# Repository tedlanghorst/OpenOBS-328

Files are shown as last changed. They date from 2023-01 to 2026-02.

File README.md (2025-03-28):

# OpenOBS-328

OpenOBS-328 is the successor to the [OpenOBS](http://www.github.com/tedlanghorst/openobs) project, an opensource, field-deployable, optical backscatter sensor (OBS). OBSs are used for measuring the turbidity, or clarity, of water for environmental monitoring. Here you will the find folders for the PCB assembly files, sensor firmware, and processing scripts.

**For more information on building, deploying, and using the sensor, visit our [documentation page!](https://tedlanghorst.github.io/OpenOBS-328/)**

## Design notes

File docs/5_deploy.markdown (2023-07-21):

---
layout: page
title: Deploy
permalink: /deploy/
---

## Introduction
{:.no_toc}

This guide will take you through programming an OpenOBS-328 sensor for deployment. You will need a computer (preferably windows), a micro usb cable, an OpenOBS-328, and a AA-sized Li-ion or LiSOCL2 battery. If you have a windows computer, you can use the graphical user interface (GUI) to quickly deploy or update the firmware. Alternatively, you can compile and upload the source code directly.

**Most of this guide describes setting up your computer, which requires an internet connection for downloading files and troubleshooting issues. You will only need to do these steps once per computer.**

## Table of Contents 
{:.no_toc}
* TOC
{:toc}

## Programming
At this stage, your OpenOBS-328 should have the firmware installed, but still we need to update the current time and send over our deployment settings. The GUI is the easiest and fastest way to upload settings, or even flash pre-compiled firmware, but only works on Windows computers. On other platforms, or if you need more control over the logger firmware, you can edit the firmware, recompile, and upload using the Arduino code editor.

---
### GUI
#### Setup
1. All of the latest OpenOBS GUI files and documentation are available in a seperate [github repo](https://github.com/tedlanghorst/OpenOBS-GUI). Download the github repository and then navigate to *OpenOBS-GUI/bin/* and try to run the *OpenOBS_328_GUI.exe* application. The program will only run on a Windows computer with the .NET 5 Desktop Runtime. If you don’t have the correct runtime, an error will pop up and direct you to the download page.

1. Connect an OpenOBS-328 sensor to your computer with a micro USB cable to test your setup.

1. Click the dropdown menu at the top of the deploy GUI and select the COM port that corresponds to the OpenOBS. You can identify the right port by trial and error (press the connect button and wait a few seconds), or by noting the available COM ports, disconnecting the OpenOBS, opening the dropdown again to refresh the list, and checking which COM port has disappeared. 
    * If you can not find the OpenOBS COM port, you likely need to download and install the [CH340 USB-Serial driver](https://learn.sparkfun.com/tutorials/how-to-install-ch340-drivers/all#drivers-if-you-need-them) on your computer.
    * If you still can not find the COM port, you may need to reflash the firmware on the sensor. Try following the steps in the next [next section.](#arduino-code)
1. After connecting to an OpenOBS, the sensor will go through a startup and self checkout before letting you program it. Any errors will be displayed on the right side of the GUI along with possible solutions. If there are no errors, the “Send Settings” button will be enabled and turn green while the sensor waits for you to choose the deployment settings:

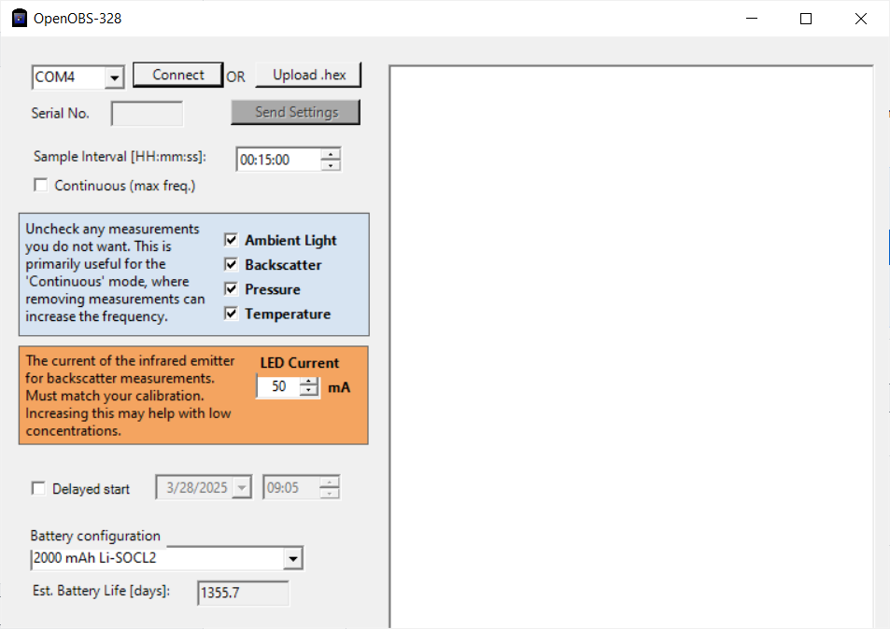
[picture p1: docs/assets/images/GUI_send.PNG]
Connected GUI
    

1. At this point you have successfully set up the deployment GUI. Good job! If you use the same USB port in the future, the COM port should be the same every time you connect an OpenOBS.

#### Deploying
1. Open the OpenOBS and slide the circuit board out of the PVC housing. Install a 3.6V Li-SOCl2 or 3.7V Li-ion AA-size battery. 
    >:warning: A regular 1.5V AA battery (even the lithium types) will not work. The USB connection provides power while plugged in, so you will not have any indication that the battery is working while programming the sensor. 
1. Connect the OpenOBS Arduino and the computer with a micro USB cable.
1. Open the deployment GUI program.
1. Select the correct COM port and click “Connect”.
1. If there are no errors on startup, the “Send Settings” button will be enabled and turn green while the sensor waits for you to choose the deployment settings.
1. Enter your sampling interval. Select delayed start if you want the logger to sleep until the set time. In addition to setting the measurement interval, sending the settings to the OpenOBS synchronizes the clock with your computer. Make sure your computer time is accurate and set to your time zone of choice, as there are no time zones recorded on the OpenOBS.
1. Selecting the battery from the dropdown will give you an estimate of the battery life. Be conservative with these numbers, they are extrapolations of short term measurements and not fully tested. Our best estimates (and tests) of battery life are here:

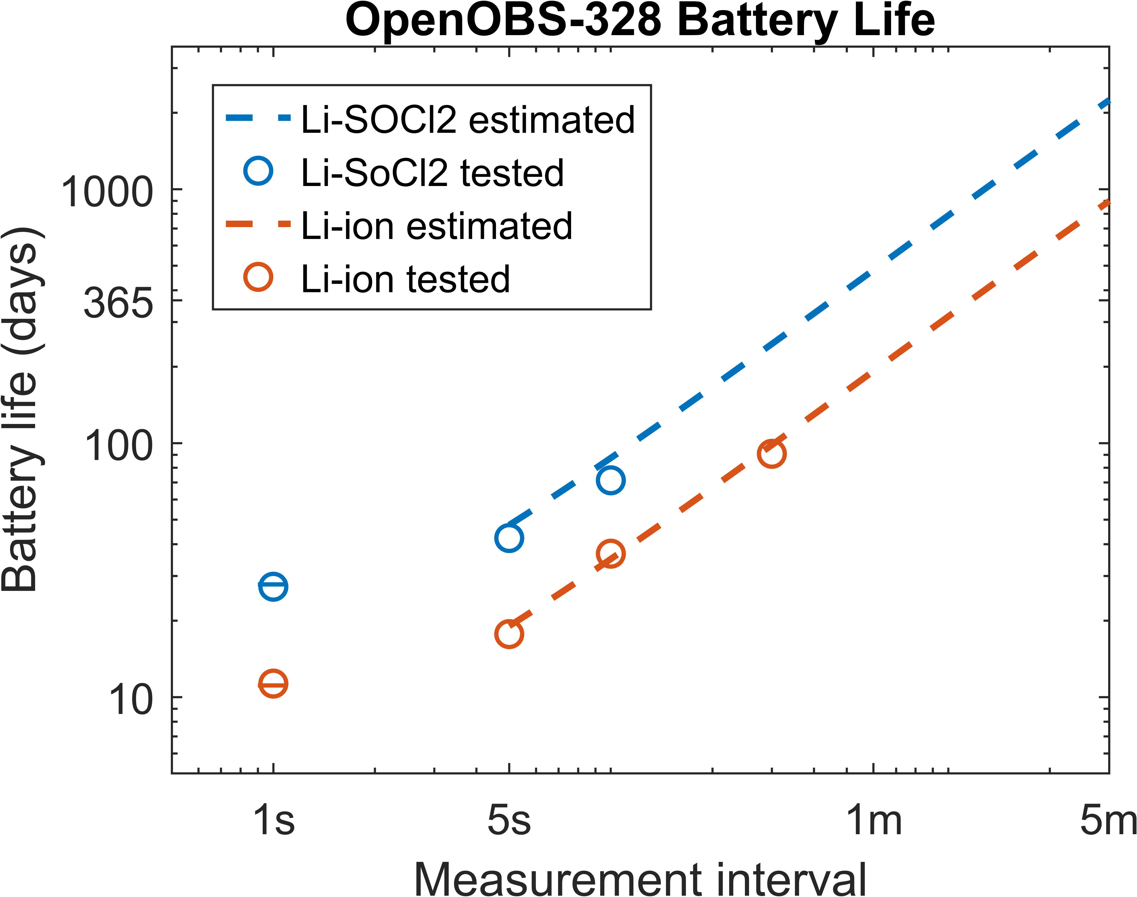
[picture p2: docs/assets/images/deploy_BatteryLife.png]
battery life
    

1. Click “Send Settings”. The OpenOBS will print out raw data when it logs while connected, refer to the [data page](./5_data.markdown) to interpret it. 

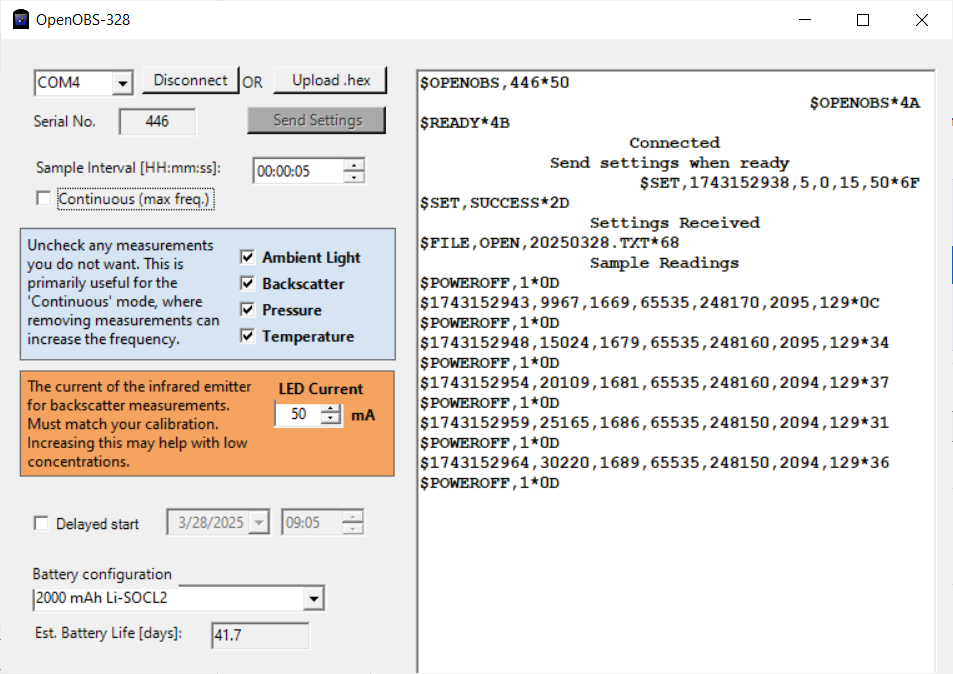
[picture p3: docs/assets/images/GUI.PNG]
programmed sensor
    

### Arduino Code
1. This option is nearly identical to the steps required to set up a newly-constructed sensor. Follow the programming directions on the [build page](./2_build.markdown#programming).
1. Change the variable *sleepDuration_seconds* to set the measurement interval. 
1. Change *delayedStart_seconds* if desired.
1. When you upload the code, the compiler will take the time from your computer, so make sure it is accurate and in the right time zone you want to record in the data.

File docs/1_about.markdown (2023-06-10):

---
layout: page
title: About
permalink: /about/
---

OpenOBS is an academic research project to develop an open source, affordable, and accurate turbidity and water level sensor using common electronics components. Turbidity (which can be calibrated to the concentration of suspended particulate matter) and water level (which can be calibrated to river discharge) are key components of monitoring a river system. Increased flow in the river raises the water level, and at the same time, washes sediment and other matter downstream. OpenOBS-328 allows us to cheaply and effectively monitor both of these effects. While comparable commercial sensors cost upwards of $2000, OpenOBS can be built for about $50 and a couple hours of work. 

&nbsp;

# History 
The project began at the University of North Carolina at Chapel Hill (UNC) under the direction of Dr. Evan Goldstein and Dr. Emily Eidam in 2019. After a long period of design and testing, we started producing dozens of sensors and published [the first OpenOBS manuscript](https://aslopubs.onlinelibrary.wiley.com/doi/abs/10.1002/lom3.10469) in Limnology and Oceanography Methods. By 2022, we had built almost 90 sensors and deployed them many times in North Carolina and Alaska, USA. Constructing each sensor was labor intensive and often required troubleshooting problems after assembly. Further, readings were highly sensitive to ambient light and affected by changes in temperature. 

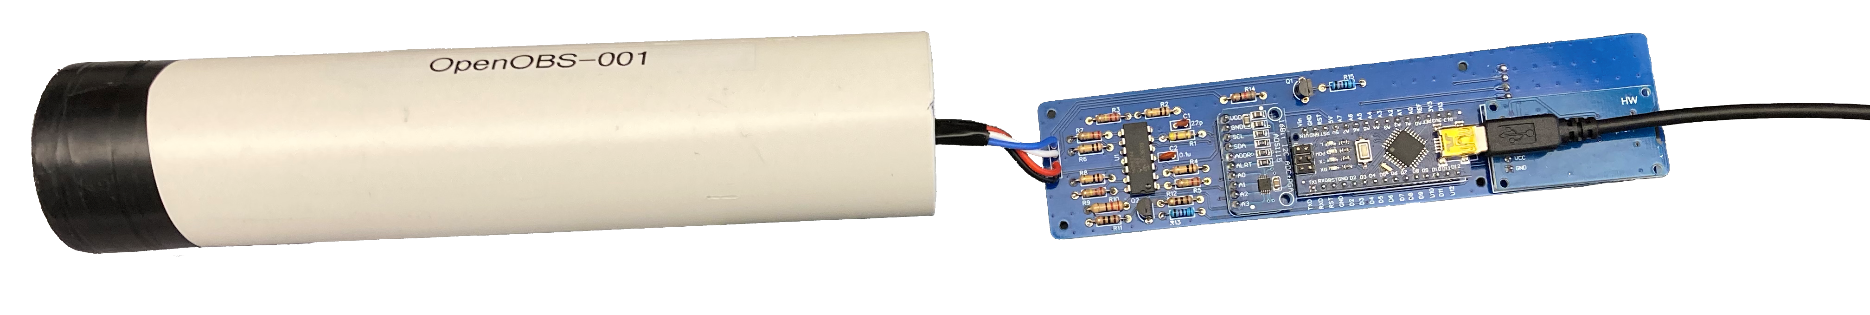
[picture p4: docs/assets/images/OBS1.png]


*The Original OpenOBS sensor ([GitHub repo](https://github.com/tedlanghorst/OpenOBS)).*

&nbsp;

Development of the OpenOBS-328 began in Fall 2022 when Dr. Emily Eidam was awarded an NSF grant which provided funding to continue developement of the OpenOBS sensor. This included the addition of the pressure sensor and a variant that transmits data in real time. At this point, we decided to move on from many of the old design decisions and approach the problem again with our new knowledge. We changed from a discrete implementation of a photodiode and signal amplifier to an integrated solution (the VCNL4010), which uses the same measurement principles and handles all the analog sensing. We also transitioned from hand-soldering modules on a printed circuit board (PCB) to an entirely assembled PCB that integrated the same functions in a smaller package.

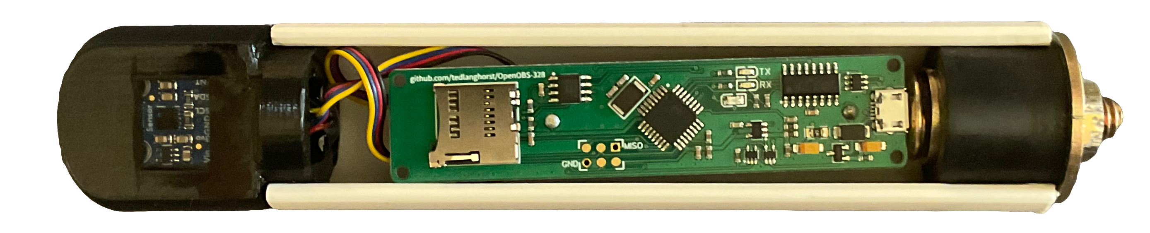
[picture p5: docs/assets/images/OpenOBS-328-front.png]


*The new OpenOBS-328 sensor.*

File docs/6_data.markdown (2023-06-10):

---
layout: page
title: Data
permalink: /data/
---

## Data format
Data is saved on the micro SD card as a .TXT file. A new file is created every day at midnight with the format YYYYMMDD. The data files should look something like this: 
~~~
If found, please contact XXXXX
Firmware updated: 2023/02/27
OpenOBS SN:000

time,ambient_light,backscatter,pressure,water_temp,battery
1677518326,1307,11354,9823,2145,649
1677518327,1300,11360,9826,2145,641
1677518328,2402,11296,9824,2145,639
1677518329,3068,11273,9824,2145,639
1677518330,2218,11287,9823,2146,639
~~~

After the data header, we have columns of data that represent
* time (Posix/Unix time. seconds since Jan 1, 1970)
* ambient light (light from 400-700 nm. Appx. equal to 1-2 Lux per unit)
* backscatter (uncalibrated backscatter intensity. Linear w.r.t. turbidity)
* pressure (bar * 10<sup>-5</sup>)
* water temperature (C * 10<sup>-1</sup>)
* battery level (multiply by 3.3*2<sup>-9</sup> to get Volts)

*There is an intermittent bug in the firmware that occasionally omits the header. If this happens, don't worry. The data rows are unaffected and you can copy a header over from another day (make sure you keep the serial number the same).*

## Iridium logger data
The Iridium data logger uses the same sensor head as the 328 version, but with an additional air pressure and temperature sensor for water level correction. As such, the data files on the micro-SD card look very similar to the 328 data. 
The data transmitted from the Iridium loggers is the same as stored on the micro-SD card, but has to be unpacked after transmitting. Rockblock charges about $0.12 per 50 bytes of data transmitted, so we use bit field structures to pack the data down to the smallest possible size without losing information. Each data record is packed into 16 bytes as follows: 

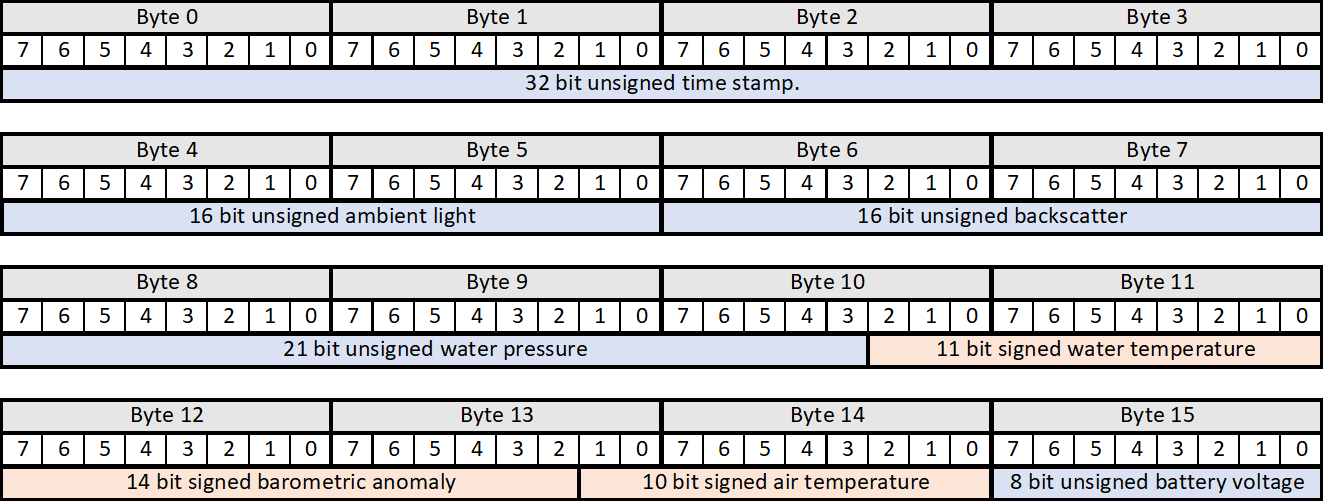
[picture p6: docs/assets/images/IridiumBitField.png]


The Iridium loggers batch these data and transmits 3 sets of 16 bytes (48 bytes) at once, to fit nicely in the 50 byte Iridium package. When you receive the data, it will have some header info and then a string of characters representing the bytes in hexadecimal. You will need to process the data according to the image above before using it.

Below is an example script in python that parses the data using the ctypes package and carefully recreating our data structure and union with a byte array. This mimicks what happens when we package the data before transmitting, except instead of putting measurements into the records in our transmission packet, we put the data string into the packet. Then, we can access the measurements records through the packet union object.

~~~python

import ctypes as ct

#example data
dataString = "320254641900E72A8884811B2FFF36883E0254641900F52A8784811B36FF3685480254641A00F82A8A84811B34BF3685"
dataBytes = bytes.fromhex(dataString)
nBytes = len(dataBytes)

#recreate the data structure from the Arduino data logger
class single_record(ct.LittleEndianStructure):
    _fields_ = [("logtime", ct.c_uint32, 32),
                ("tuBackground", ct.c_uint32, 16),
                ("tuBackscatter", ct.c_uint32, 16),
                ("waterPressure", ct.c_uint32, 21),
                ("waterTemp",ct.c_int32, 11),
                ("baroAnomaly",ct.c_int32,14),
                ("airTemp",ct.c_int32,10),
                ("batteryVoltage",ct.c_uint32,8)]  
    
class transmission_packet(ct.Union):
    _fields_ = [("record", single_record*(nBytes//ct.sizeof(single_record))),
                ("data", ct.c_ubyte*nBytes)]

#Create a packet object and put our data in as a byte array.
packet = transmission_packet()
packet.data = (ct.c_ubyte * nBytes)(*dataBytes)

#example data access
print(packet.record[0].logtime)

#show all the data
for r in packet.record:
    for f in r._fields_:
        print('{:<20s}{:d}'.format(f[0], getattr(r, f[0])))

~~~

## Processing scripts
Some basic processing scripts for Matlab and Python are found [here](https://github.com/tedlanghorst/OpenOBS-328/tree/main/scripts). I try to keep these updated but variations in sensor versions and development can make it messy. Check over the data headers and conversions if you use them.

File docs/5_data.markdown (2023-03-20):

---
layout: page
title: Data
permalink: /data/
---

## Data format
Data is saved on the micro SD card as a .TXT file. A new file is created every day at midnight with the format YYYYMMDD. The data files should look something like this: 
~~~
If found, please contact tlang@live.unc.edu
Firmware updated: 2023/02/27
OpenOBS SN:000

time,ambient_light,backscatter,pressure,water_temp,battery
1677518326,1307,11354,9823,2145,649
1677518327,1300,11360,9826,2145,641
1677518328,2402,11296,9824,2145,639
1677518329,3068,11273,9824,2145,639
1677518330,2218,11287,9823,2146,639
~~~

After the data header, we have columns of data that represent
* time (Posix/Unix time. seconds since Jan 1, 1970)
* ambient light (light from 400-700 nm. Appx. equal to 1-2 Lux per unit)
* backscatter (uncalibrated backscatter intensity. Linear w.r.t. turbidity)
* pressure (bar * $10^{-5}$)
* battery (multiply by $\frac{3.3}{2^{9}}$ to get Volts)

*There is an intermittent bug in the firmware that occasionally omits the header. If this happens, don't worry. The data rows are unaffected and you can copy a header over from another day (make sure you keep the serial number the same).*

## Processing scripts
Some basic processing scripts for Matlab and Python are found [here](http://www.github.com). I try to keep these updated but variations in sensor versions and development can make it messy. Check over the data headers and conversions if you use them.

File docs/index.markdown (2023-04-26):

---
# Feel free to add content and custom Front Matter to this file.
# To modify the layout, see https://jekyllrb.com/docs/themes/#overriding-theme-defaults

layout: home
permalink: 
---

Welcome to the OpenOBS documentation site! Browse the pages linked in the header for information about the project, how to build your own OpenOBS, and how to use the sensors. 

If you find an error or have a problem with any part of the project, please let us know by [**opening a new issue**](https://github.com/tedlanghorst/OpenOBS-328/issues/new). This leaves a public record of outstanding issues and solutions that can help others. 



---
&nbsp; 

OpenOBS is published under the [GNU GPL v3 license](https://www.gnu.org/licenses/gpl-3.0.en.html). In short, this license ensures the freedom of use and distribution of this project forever. You can copy this work exactly or modify it (maybe replace the image of my dog with yours), give it away or sell it; what you cannot do is redistribute the OpenOBS, or a derivative of it, without these same freedoms.

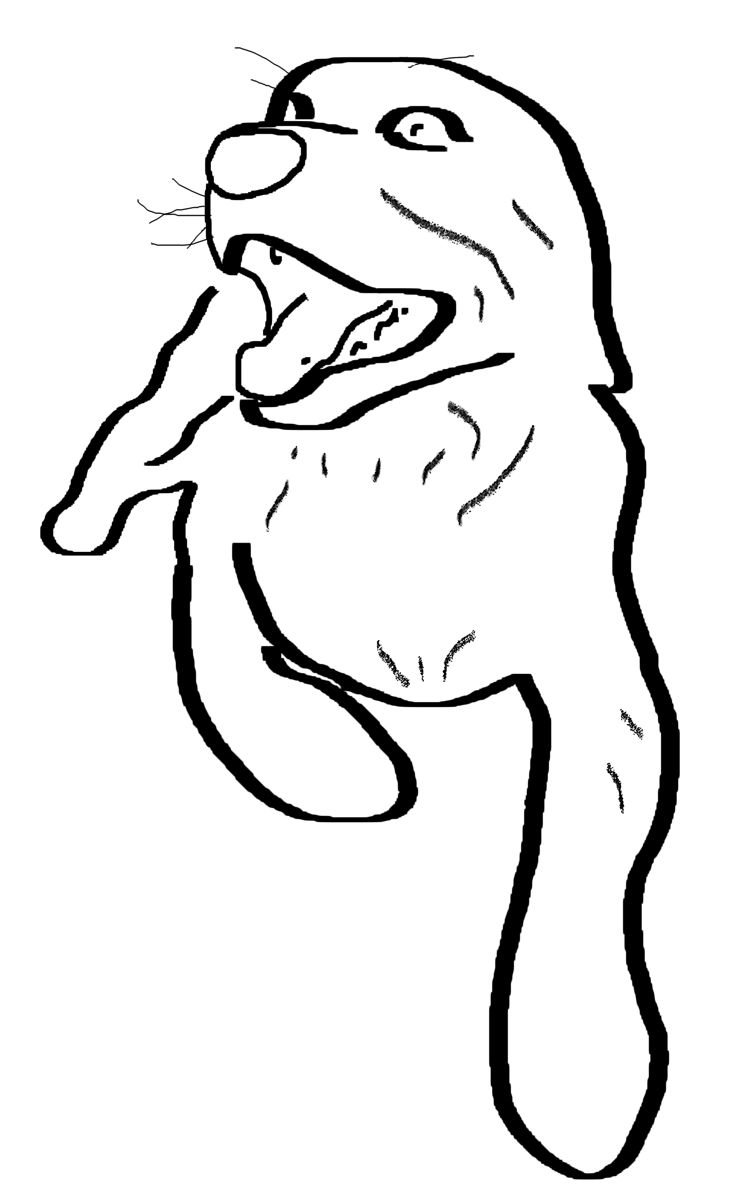
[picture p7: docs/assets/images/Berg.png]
BERG!
<p style="text-align:center;"> BERG! </p>

<!--https://docs.github.com/en/pages/setting-up-a-github-pages-site-with-jekyll/testing-your-github-pages-site-locally-with-jekyll-->

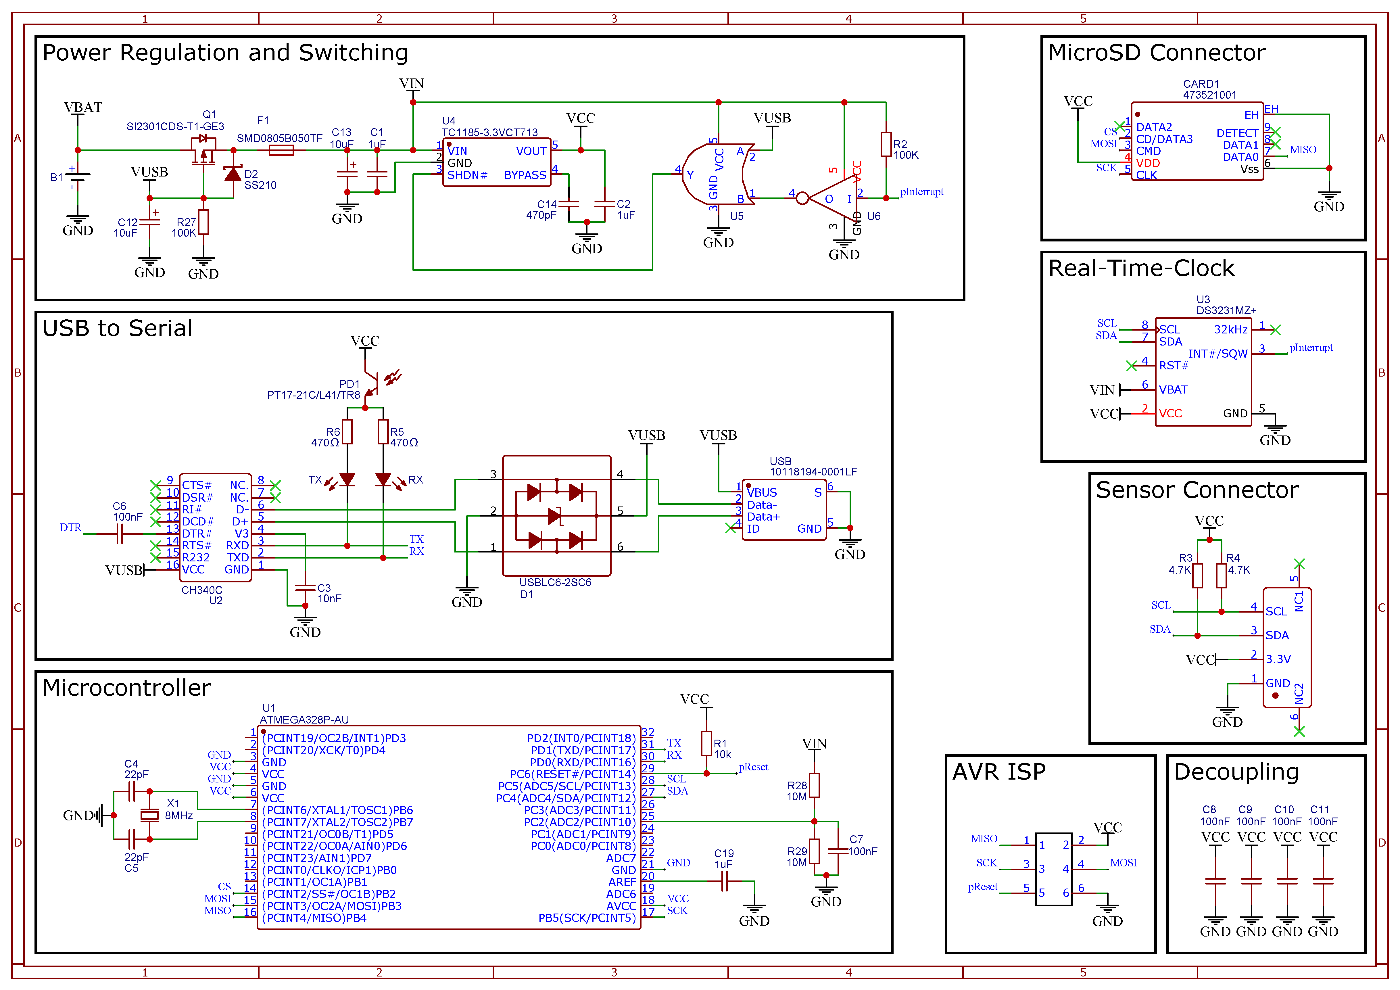
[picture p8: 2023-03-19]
docs/assets/images/Schematic_OpenOBS_328p_Tanana_2023-02-04.png

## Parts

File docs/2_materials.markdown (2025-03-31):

---
layout: page
title: Materials
permalink: /materials/
---
## Introduction
{:.no_toc}
The parts cost of an OpenOBS-328 is approximately $50 USD. This can be slightly reduced in larger quantities ($40 at 50 qty). You will also need tools and equipment to build your sensors, which we have tried to reduce to the essentials here. These costs are substantial, especially if you are trying to build just a few sensors. If you don't have a lot of this equipment and aren't looking to invest in these tools, look into community resources. For example, the Univeristy of North Caorlina at Chapel Hill has a 'makerspace' with most of these tool available. Similar spaces and tool sharing communities exist outside of univiersities. 

## Table of Contents 
{:.no_toc}
* TOC
{:toc}

## Tools & Materials
* Soldering iron
* Solder
* Hot air gun/station for electronics. (sometimes called rework station)
* No clean solder paste
* Vacuum pump
* Vacuum chamber
* disposable pipettes (3 mL size works well)
* Hot glue gun
* 3D printer
* PVC pipe cutter (can use a saw)
* PVC cement/solvent
* Electronics tweezers
* Fine flush cutters
* Wire strippers (22-30 AWG)
* Electrical tape
* micro USB cable
* Arduino Nano (or clone; [for ISP programmer](./3_build.markdown#isp-programmer))
* Pogo pins (6 individual or 2x3 grid)

## Parts

<style type="text/css">
.tg  {border-collapse:collapse;border-spacing:0;}
.tg td{border-color:black;border-style:solid;border-width:1px;font-family:Arial, sans-serif;font-size:14px;
  overflow:hidden;padding:10px 5px;word-break:normal;}
.tg th{border-color:black;border-style:solid;border-width:1px;font-family:Arial, sans-serif;font-size:14px;
  font-weight:normal;overflow:hidden;padding:10px 5px;word-break:normal;}
.tg .tg-wp8o{border-color:#000000; text-align:center;vertical-align:top}
.tg .tg-73oq{border-color:#000000;text-align:left;vertical-align:top}
.tg .tg-jdb5{border-color:#000000;font-weight:bold;text-align:center;vertical-align:bottom; border-width: 0px 0px 5px 0px}
.tg .tg-1tol{border-color:#000000;font-weight:bold;text-align:left;vertical-align:middle}
.tg .tg-4e6d{border-color:#000000;color:#00E;text-align:left;text-decoration:underline;vertical-align:top}
.tg .tg-noSides{border-left:0px; border-right:0px}
</style>
<table class="tg">
<colgroup>
<col style="width: 15%">
<col style="width: 20%">
<col style="width: 10%">
<col style="width: 10%">
<col style="width: 20%">
</colgroup>
<thead>
  <tr>
    <th class="tg-jdb5"></th>
    <th class="tg-jdb5">Item</th>
    <th class="tg-jdb5">Appx. Cost</th>
    <th class="tg-jdb5">Links</th>
    <th class="tg-jdb5">Notes</th>
  </tr>
</thead>
<tbody>
  <tr>
    <td class="tg-1tol" rowspan="10">Sensor head</td>
    <td class="tg-73oq">3D printed head</td>
    <td class="tg-wp8o">0.50</td>
    <td class="tg-73oq"><a href="https://github.com/tedlanghorst/OpenOBS-328/tree/main/sensor/hardware/3D_print/custom_pcbs" target="_blank" rel="noopener noreferrer">files</a></td>
    <td class="tg-73oq"></td>
  </tr>
  
  <tr>
    <td class="tg-73oq">m3x6 bolt</td>
    <td class="tg-wp8o">0.10</td>
    <td class="tg-73oq"><a href="https://www.amazon.com/Socket-Screws-Bolts-Thread-100pcs/dp/B07CMRQ3TB?crid=85QEXH6R1XAD&th=1" target="_blank" rel="noopener noreferrer">Gerber files</a></td>
    <td class="tg-73oq">ordering instructions below</td>
  </tr>
  <tr>
    <td class="tg-73oq">Light sensor</td>
    <td class="tg-wp8o">2.50</td>
    <td class="tg-73oq"><a href="https://github.com/tedlanghorst/OpenOBS-328/tree/main/sensor/hardware/PCBA/turbidity" target="_blank" rel="noopener noreferrer">Gerber files</a></td>
    <td class="tg-73oq">ordering instructions below</td>
  </tr>
  <tr>
    <td class="tg-73oq">pressure PCB</td>
    <td class="tg-wp8o">0.40</td>
    <td class="tg-73oq"><a href="https://github.com/tedlanghorst/OpenOBS-328/tree/main/sensor/hardware/PCBA/pressure" target="_blank" rel="noopener noreferrer">Gerber files</a></td>
    <td class="tg-73oq">ordering instructions below</td>
  </tr>
  <tr>
    <td class="tg-73oq">pressure sensor</td>
    <td class="tg-wp8o">21</td>
    <td class="tg-73oq"><a href="https://octopart.com/ms580314ba01-00-te+connectivity-59208930?r=sp" target="_blank" rel="noopener noreferrer">14 bar</a><br><a href="https://octopart.com/ms580305ba01-00-te+connectivity-59208929?r=sp" target="_blank" rel="noopener noreferrer">5 bar</a></td>
    <td class="tg-73oq">5 bar max sensor has better resolution</td>
  </tr>
  <tr>
    <td class="tg-73oq">flat flex cable</td>
    <td class="tg-wp8o">0.61</td>
    <td class="tg-73oq"><a href="https://octopart.com/search?q=5-1474644-0&currency=USD&specs=0" target="_blank" rel="noopener noreferrer">octopart</a></td>
    <td class="tg-73oq"></td>
  </tr>
  <tr>
    <td class="tg-73oq">0603 0.1uF</td>
    <td class="tg-wp8o">0.01</td>
    <td class="tg-73oq"><a href="https://octopart.com/cl10b104kb8nnwc-samsung-23795471?r=sp" target="_blank" rel="noopener noreferrer">octopart</a></td>
    <td class="tg-73oq">Very generic part. Any 0603 0.1uF will do.</td>
  </tr>
  <tr>
    <td class="tg-73oq">epoxy</td>
    <td class="tg-wp8o">0.50</td>
    <td class="tg-73oq"><a href="https://www.amazon.com/dp/B07RM5Z991" target="_blank" rel="noopener noreferrer">750g</a><br><a href="https://www.amazon.com/dp/B079Y9QFQS/" target="_blank" rel="noopener noreferrer">1500g</a></td>
    <td class="tg-73oq">~20g per sensor</td>
  </tr>
  <tr>
    <td class="tg-73oq">1" PVC</td>
    <td class="tg-wp8o">0.40</td>
    <td class="tg-73oq"><a href="https://www.lowes.com/pd/1-in-dia-x-10-ft-L-450-PSI-PVC-Pipe/3133091" target="_blank" rel="noopener noreferrer">Lowe's</a></td>
    <td class="tg-73oq">6" per sensor</td>
  </tr>
  <tr>
    <td class="tg-73oq">pvc cement</td>
    <td class="tg-wp8o">0.20</td>
    <td class="tg-73oq"><a href="https://www.lowes.com/pd/Oatey-8-fl-oz-PVC-Cement/4750803" target="_blank" rel="noopener noreferrer">Lowe's</a></td>
    <td class="tg-73oq">cost based on 50 sensors</td>
  </tr>
  <tr>
    <td class="tg-noSides"></td>
    <td class="tg-noSides"></td>
    <td class="tg-noSides"></td>
    <td class="tg-noSides"></td>
    <td class="tg-noSides"></td>
  </tr>
  <tr>
    <td class="tg-1tol" rowspan="5">OpenOBS-328</td>
    <td class="tg-73oq">assembled PCB</td>
    <td class="tg-wp8o">12</td>
    <td class="tg-73oq"><a href="https://github.com/tedlanghorst/OpenOBS-328/tree/main/sensor/hardware/PCBA/logger" target="_blank" rel="noopener noreferrer">Gerber files</a></td>
    <td class="tg-73oq">ordering instructions below</td>
  </tr>
  <tr>
    <td class="tg-73oq">Battery holder</td>
    <td class="tg-wp8o">1.1</td>
    <td class="tg-73oq"><a href="https://octopart.com/2460-keystone-17876?r=sp" target="_blank" rel="noopener noreferrer">Octopart</a></td>
    <td class="tg-73oq"></td>
  </tr>
  <tr>
    <td class="tg-73oq">qwiic connector</td>
    <td class="tg-wp8o">0.5</td>
    <td class="tg-73oq"><a href="https://octopart.com/sm04b-srss-tb%28lf%29%28sn%29-jst-289307?r=sp" target="_blank" rel="noopener noreferrer">Octopart</a></td>
    <td class="tg-73oq"></td>
  </tr>
  <tr>
    <td class="tg-73oq">qwiic cable (JST SH connector 4 pin 20cm length)</td>
    <td class="tg-wp8o">1</td>
    <td class="tg-73oq"><a href="https://octopart.com/prt-17257-sparkfun-115856491?r=sp" target="_blank" rel="noopener noreferrer">Octopart</a><br>
    <a href="https://www.sparkfun.com/products/14429" target="_blank" rel="noopener noreferrer">Sparkfun</a><br>
    <a href="https://www.aliexpress.us/item/3256803220110303.html" target="_blank" rel="noopener noreferrer">AliExpress</a>
    </td>
    <td class="tg-73oq">Can cut in half, need ~20 cm length. Double check options if using AliExpress. </td>
  </tr>
  <tr>
    <td class="tg-73oq">end plug</td>
    <td class="tg-wp8o">3.5</td>
    <td class="tg-73oq"><a href="https://www.amazon.com/dp/B09P12JQRD" target="_blank" rel="noopener noreferrer">Amazon</a></td>
    <td class="tg-73oq"></td>
  </tr>
  <tr>
    <td class="tg-noSides"></td>
    <td class="tg-noSides"></td>
    <td class="tg-noSides"></td>
    <td class="tg-noSides"></td>
    <td class="tg-noSides"></td>
  </tr>
  <tr>
    <td class="tg-1tol" rowspan="7">Iridium</td>
    <td class="tg-73oq">iridium module</td>
    <td class="tg-wp8o">267.5</td>
    <td class="tg-73oq"><a href="https://www.sparkfun.com/products/14498" target="_blank" rel="noopener noreferrer">Sparkfun</a></td>
    <td class="tg-73oq">+ $15/month and $0.12/transmission</td>
  </tr>
  <tr>
    <td class="tg-73oq">pressure sensor (baro)</td>
    <td class="tg-wp8o">22</td>
    <td class="tg-73oq"><a href="https://octopart.com/ms580302ba01-00-te+connectivity-59208928?r=sp" target="_blank" rel="noopener noreferrer">Octopart</a></td>
    <td class="tg-73oq"></td>
  </tr>
  <tr>
    <td class="tg-73oq">qwiic cable</td>
    <td class="tg-wp8o">1</td>
    <td class="tg-4e6d"><a href="https://octopart.com/prt-17257-sparkfun-115856491?r=sp" target="_blank" rel="noopener noreferrer">Octopart</a><br><a href="https://www.sparkfun.com/products/14429" target="_blank" rel="noopener noreferrer">Sparkfun</a></td>
    <td class="tg-73oq">Cut in half, 1 part supplies 2 sensors.</td>
  </tr>
  <tr>
    <td class="tg-73oq">100' cable</td>
    <td class="tg-wp8o">35</td>
    <td class="tg-4e6d"><a href="https://www.amazon.com/Monoprice-Access-Gauge-Conductor-Speaker/dp/B003KPYRJM/ref=d_pd_di_sccai_cn_sccl_2_2/147-5558742-6438149?pd_rd_w=XtCA6&content-id=amzn1.sym.e13de93e-5518-4644-8e6b-4ee5f2e0b062&pf_rd_p=e13de93e-5518-4644-8e6b-4ee5f2e0b062&pf_rd_r=2148BS7ECTT29JE6CXV4&pd_rd_wg=w4b3d&pd_rd_r=52dbf083-5f28-4a72-8769-5486458894c5&pd_rd_i=B003KPYRJM&psc=1" target="_blank" rel="noopener noreferrer">Amazon</a></td>
    <td class="tg-73oq"></td>
  </tr>
  <tr>
    <td class="tg-73oq">case</td>
    <td class="tg-wp8o">30</td>
    <td class="tg-4e6d"><a href="https://www.amazon.com/Olympia-Waterproof-Customizable-Equiment-Camera/dp/B08CXZNSK2/ref=sr_1_15?crid=JHF3WLPXNAAT&keywords=waterproof%2Bcase&qid=1683414354&sprefix=waterproof%2Bcase%2Caps%2C98&sr=8-15&th=1" target="_blank" rel="noopener noreferrer">Amazon</a></td>
    <td class="tg-73oq"></td>
  </tr>
  <tr>
    <td class="tg-73oq">solar panel</td>
    <td class="tg-wp8o">38</td>
    <td class="tg-4e6d"><a href="https://www.amazon.com/SOLPERK-Maintainer-Waterproof-Controller-Adjustable/dp/B091KGZGM3/ref=sr_1_3?crid=2H0AH8F0C328Y&keywords=12v%2Bsolar%2Bpanel&qid=1683414390&sprefix=12v%2Bsolar%2Bpanel%2Caps%2C103&sr=8-3&th=1" target="_blank" rel="noopener noreferrer">Amazon</a></td>
    <td class="tg-73oq"></td>
  </tr>
  <tr>
    <td class="tg-73oq">12V SLA battery</td>
    <td class="tg-wp8o">50</td>
    <td class="tg-4e6d"></td>
    <td class="tg-73oq"></td>
  </tr>
</tbody>
</table>

## Ordering PCBs from JLCPCB
1. Download the manufacturing files for the [data logger](https://github.com/tedlanghorst/OpenOBS-328/tree/main/sensor/hardware/PCBA/logger), [turbidity sensor](https://github.com/tedlanghorst/OpenOBS-328/tree/main/sensor/hardware/PCBA/turbidity), and [pressure sensor](https://github.com/tedlanghorst/OpenOBS-328/tree/main/sensor/hardware/PCBA/pressure) from the project Github repo. The data logger and turbidity sensors can be ordered assembled, and as such will have 3 files each. The pressure sensor directory only has 1 file because you have to assemble it separately.

1. Go to JLCPCB and click “Instant Quote”.

1. Upload one of gerber files at the top of the page (.zip extension). You will need to change the following settings:
    - **PCB Qty:** This is the number of **panels** you are ordering, and the actual number of finished boards will be greater. See next 2 steps. Multiply the rows and columns of Panel Format to get number of boards per panel.
    - **Delivery format:** Panel by Customer
    - **Panel Format:** This is different for each board:

        |        PCB       | Columns | Rows |
        |------------------|---------|------|
        | data logger      | 1       | 5    |
        | turbidity sensor | 5       | 4    |
        | pressure board   | 9       | 10   |
        
    - **Remove order number:** Specify a location
    - If you are ordering the pressure board, click **add to cart** and skip past the remainder of this section. If you are ordering the data logger or turbidity sensor, enable the option for **PCB Assembly** towards the bottom and continue. 
    - **PCBA type:** Standard
    - **Assembly side:** Top (Optionally both sides for the data logger)
    - **Edge Rails/Fiducials:** Added by Customer
    - Click **Confirm**. 
    - Click **Next**
    - This should take you to a page to upload upload the BOM and CPL files. They are both .csv files, named “BOM_\*.csv” and “PickAndPlace_\*.csv.” respectively. 
    - On the same page, select **File provided as** "Single Piece, pls help … "
    - Click **Process BOM & CPL**. You may get a warning that some components were not included in the BOM. This is fine, click **Continue**.
    - Now a table of the parts will be shown. Make sure they’re all selected and there are no warnings about inventory shortage etc. Send me an email if any parts are out of stock and I can check if there are any compatable replacements. 
    - Click **Next**. Now a rendering of the populated board should appear, but it will only include the first PCB on the panel. 
    - Click **Next** again and then **Save to Cart**.
1. Repeat the last section with any other PCBs you are ordering.
1. Go through checkout.

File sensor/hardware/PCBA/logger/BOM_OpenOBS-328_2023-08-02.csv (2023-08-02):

ID | Name | Designator | Footprint | Quantity | Manufacturer Part | Manufacturer | Supplier | Supplier Part | Price
1 | 1050171001 | USB1 | MICRO-USB-SMD_1050171001 | 1 | 1050171001 | MOLEX | LCSC | C505111 | 0.327
2 | NC7SZ14P5X | U2 | SC-70-5_L2.1-W1.3-P0.65-LS2.1-BR | 1 | NC7SZ14P5X | onsemi(安森美) | LCSC | C87406 | 0.49
3 | MIC5504-3.3YM5-TR | U4 | SOT-23-5_L3.0-W1.7-P0.95-LS2.8-TL | 1 | MIC5504-3.3YM5-TR | MICROCHIP(美国微芯) | LCSC | C88419 | 0.328
4 | CH340C | U7 | SOP-16_L10.0-W3.9-P1.27-LS6.0-BL | 1 | CH340C | WCH(南京沁恒) | LCSC | C84681 | 0.476
5 | 10uF | C12,C13 | CAP-SMD_L3.2-W1.6-R-RD | 2 | TAJA106K016RNJ | AVX | LCSC | C7171 | 0.097
6 | 1kΩ | R5,R6 | R0603 | 2 | 0603WAF1001T5E | UNI-ROYAL(厚声) | LCSC | C21190 | 0.001
7 | 1nF | C7 | C0603 | 1 | CL10B102KB8NNNC | SAMSUNG(三星) | LCSC | C1588 | 0.003
8 | 1MΩ | R7 | R0603 | 1 | 0603WAF1004T5E | UNI-ROYAL(厚声) | LCSC | C22935 | 0.001
9 | SI2301CDS-T1-GE3 | Q1 | SOT-23-3_L3.0-W1.7-P0.95-LS2.9-BR | 1 | SI2301CDS-T1-GE3 | VISHAY | LCSC | C10487 | 0.073
10 | SMD0805B050TF | F1 | F0805 | 1 | SMD0805B050TF | Brightking(君耀电子) | LCSC | C269104 | 0.02
11 | USBLC6-2SC6 | D1 | SOT-23-6_L2.9-W1.6-P0.95-LS2.8-BR | 1 | USBLC6-2SC6 | ST(意法半导体) | LCSC | C7519 | 0.121
12 | 74AHC1G32GW,125 | U5 | SOT-353_L2.2-W1.4-P0.65-LS2.4-BR | 1 | 74AHC1G32GW,125 | Nexperia | LCSC | C12489 | 0.065
13 | 8MHz | X1 | CRYSTAL-SMD_L5.0-W3.2 | 1 | X50328MSB2GI | YXC | LCSC | C115962 | 0.177
14 | SS210 | D2 | SMA_L4.3-W2.6-LS5.2-RD | 1 | SS210 | MDD | LCSC | C14996 | 0.024
15 | ATMEGA328P-AU | U1 | TQFP-32_L7.0-W7.0-P0.80-LS9.0-BL | 1 | ATMEGA328P-AU | MICROCHIP | LCSC | C14877 | 2.528
16 | 19-213/Y2C-CQ2R2L/3T(CY) | RX,TX | LED0603-R-RD | 2 | 19-213/Y2C-CQ2R2L/3T(CY) | EVERLIGHT(亿光) | LCSC | C72038 | 0.022
17 | 1uF | C1,C2,C19 | C0603 | 3 | CL10A105KB8NNNC | SAMSUNG | LCSC | C15849 | 0.006
18 | 10nF | C3 | C0603 | 1 | 0603B103K500NT | FH(风华) | LCSC | C57112 | 0.003
19 | 22pF | C4,C5 | C0603 | 2 | CL10C220JB8NNNC | SAMSUNG | LCSC | C1653 | 0.008
20 | 100nF | C6,C8,C9,C10,C11 | C0603 | 5 | CC0603KRX7R9BB104 | YAGEO | LCSC | C14663 | 0.002
21 | 470pF | C14 | C0603 | 1 | 0603B471K500NT | FH(风华) | LCSC | C1620 | 0.003
22 | 10k | R1 | R0603 | 1 | 0603WAF1002T5E | UniOhm | LCSC | C25804 | 0.001
23 | 4.7K | R3,R4 | R0603 | 2 | 0603WAF4701T5E | UniOhm | LCSC | C23162 | 0.001
24 | 100K | R27,R2 | R0603 | 2 | 0603WAF1003T5E | UniOhm | LCSC | C25803 | 0.001
25 | 10M | R28 | R0603 | 1 | 0603WAF1005T5E | UniOhm | LCSC | C7250 | 0.001
26 | DS3231MZ+ | U3 | SOIC-8_L4.9-W3.9-P1.27-LS6.0-BL | 1 | DS3231MZ+TRL | MAXIM(美信) | LCSC | C107410 | 2.052
27 | 473521001 | CARD1 | SD-SMD_SD-47352-101 | 1 | 473521001 | MOLEX | LCSC | C293569 | 0.835
28 | SM04B-SRSS-TB (LF)(SN) | QWIIC | CONN-SMD_4P-P1.00_SM04B-SRSS-TB-LF-SN | 1 | SM04B-SRSS-TB(LF)(SN) | JST | LCSC | C160404 | 0.178
29 | KEYSTONE 2460 1XAA | B1 | KEYSTONE 2460 1XAA | 1 | 2460 | Keystone Electronics | Digi-Key | 36-2460-ND

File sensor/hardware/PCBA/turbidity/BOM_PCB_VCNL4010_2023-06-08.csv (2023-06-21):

ID | Name | Designator | Footprint | Quantity | Manufacturer Part | Manufacturer | Supplier | Supplier Part | Price
1 | 10uF | C1 | C0603 | 1 | CL10A106MA8NRNC | SAMSUNG(三星) | LCSC | C96446 | 0.024
2 | 100nF | C2,C4 | C0603 | 2 | CC0603KRX7R9BB104 | YAGEO(国巨) | LCSC | C14663 | 0.002
3 | 22uF | C3 | C0603 | 1 | CL10A226MQ8NRNC | SAMSUNG(三星) | LCSC | C59461 | 0.01
4 | 10kΩ | R1,R2 | R0603 | 2 | 0603WAF1002T5E | UNI-ROYAL(厚声) | LCSC | C25804 | 0.001
5 | 10Ω | R3 | R0603 | 1 | 0603WAF100JT5E | UNI-ROYAL(厚声) | LCSC | C22859 | 0.001
6 | VCNL4010-GS08 | U1 | SENSORS-SMD_VCNL4010-GS08 | 1 | VCNL4010-GS08 | VISHAY(威世) | LCSC | C92131 | 1.51

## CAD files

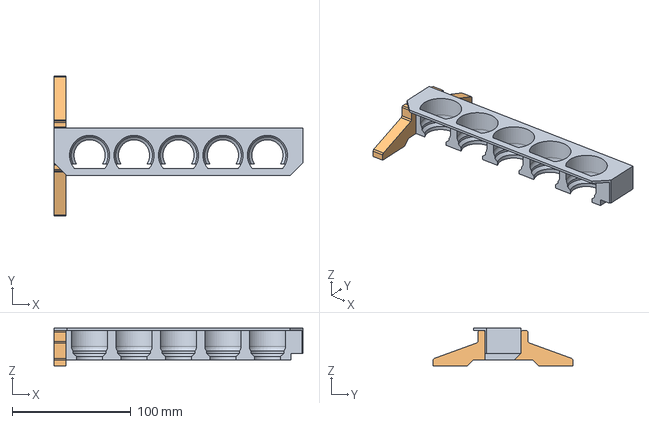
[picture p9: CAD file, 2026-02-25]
sensor/hardware/3D_print/custom_pcbs/OpenOBS_clampingCaul v10.step
210.0 x 118.0 x 32.0 mm
caul

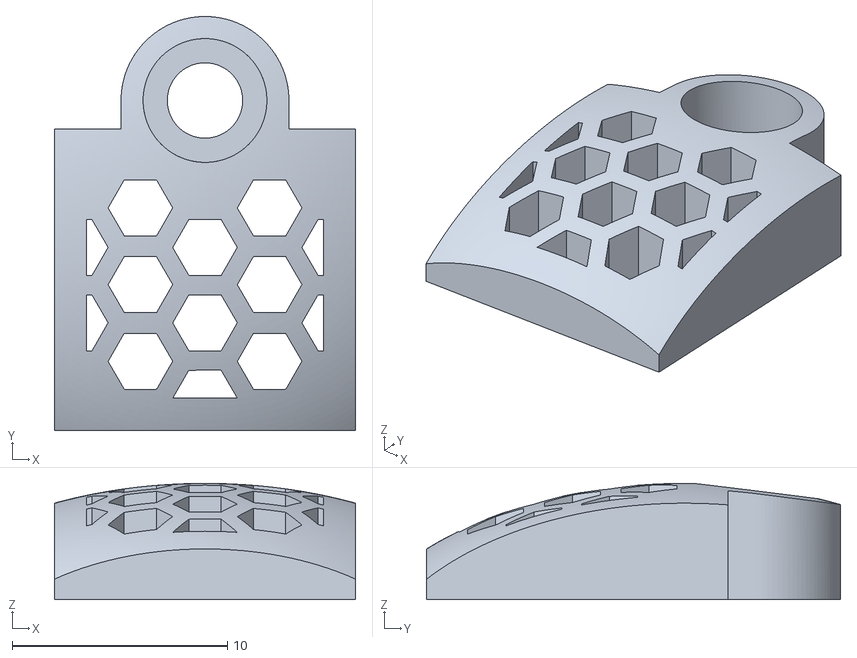
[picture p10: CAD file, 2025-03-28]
sensor/hardware/3D_print/custom_pcbs/PressureFilter_V3.stl
14.0 x 19.2 x 5.40

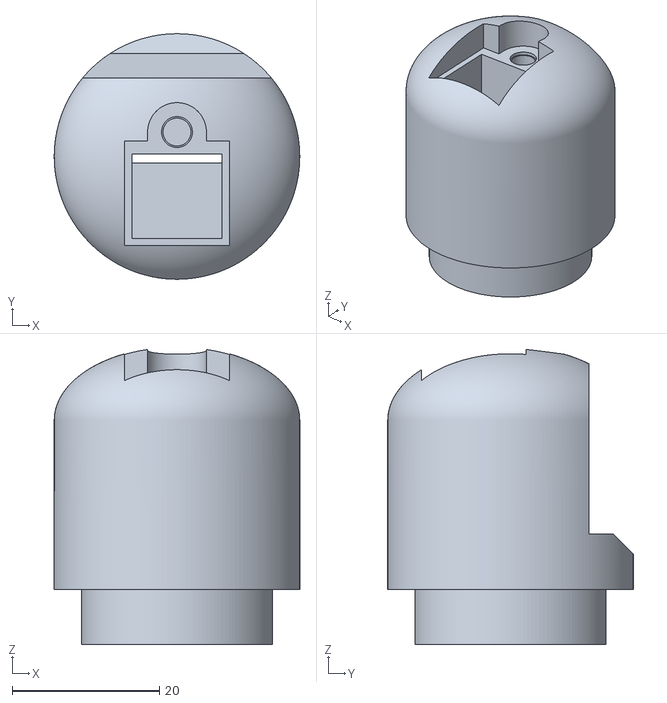
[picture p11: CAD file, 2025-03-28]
sensor/hardware/3D_print/custom_pcbs/SensorHead_V3.stl
33.4 x 33.4 x 40.1

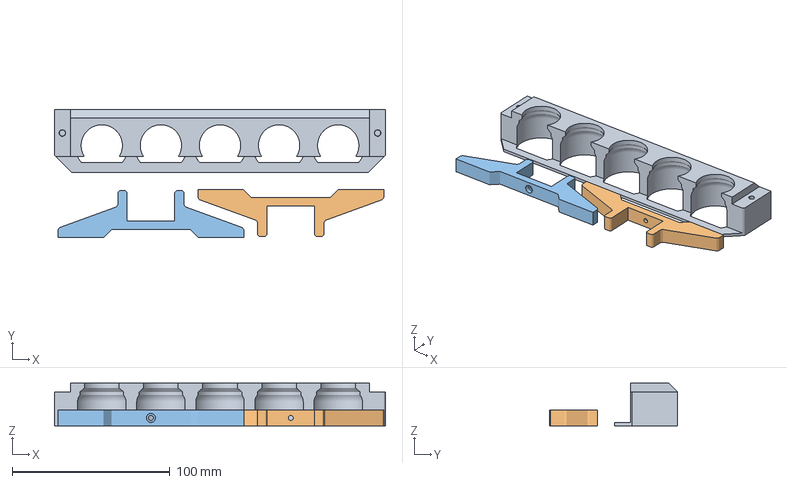
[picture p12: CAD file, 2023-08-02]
sensor/hardware/3D_print/custom_pcbs/clampingCaul_v2.3mf
210.0 x 81.4 x 27.0 mm

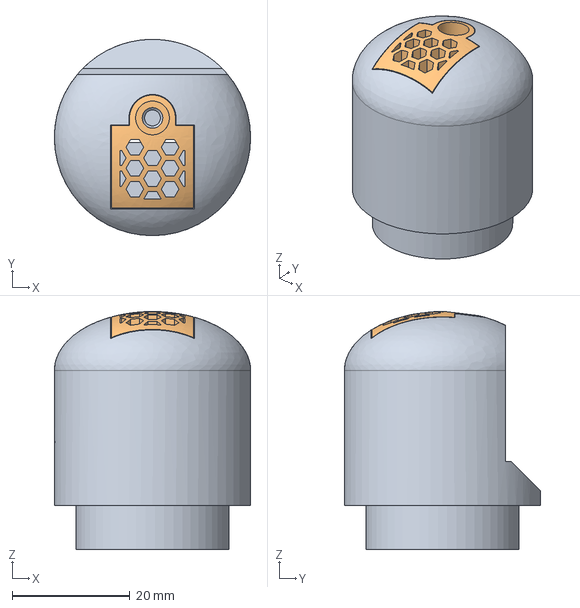
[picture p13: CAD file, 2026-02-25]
sensor/hardware/3D_print/custom_pcbs/sensorhead_v2_filterBolt v3.step
33.4 x 33.4 x 40.5 mm

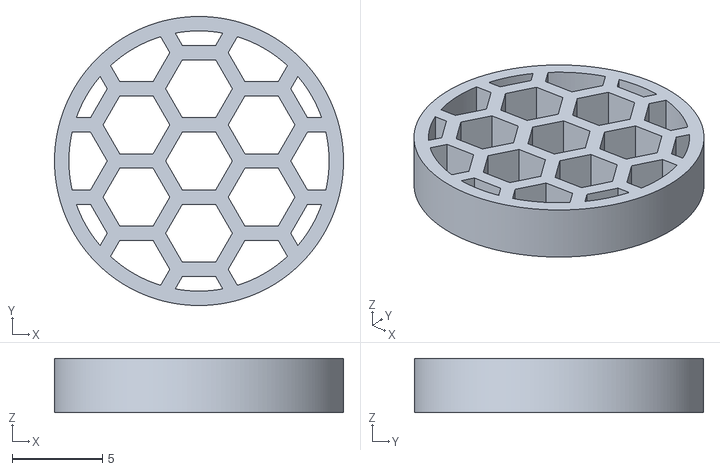
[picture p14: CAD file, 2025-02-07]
sensor/hardware/3D_print/off_the_shelf/pressure_filter.stl
16.0 x 16.0 x 3.00

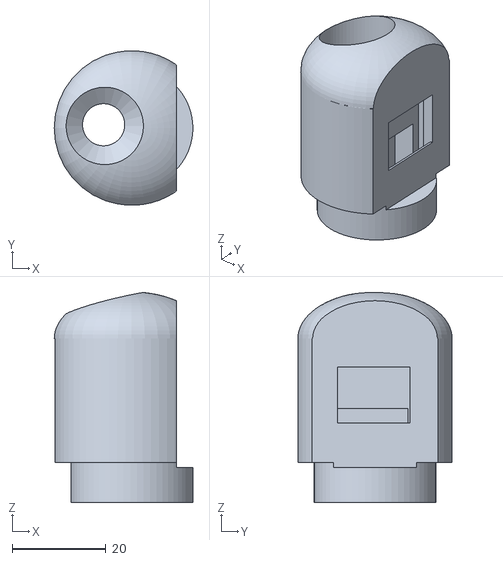
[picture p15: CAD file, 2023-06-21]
sensor/hardware/3D_print/off_the_shelf/sensorHead_v1.stl
29.6 x 33.0 x 44.9

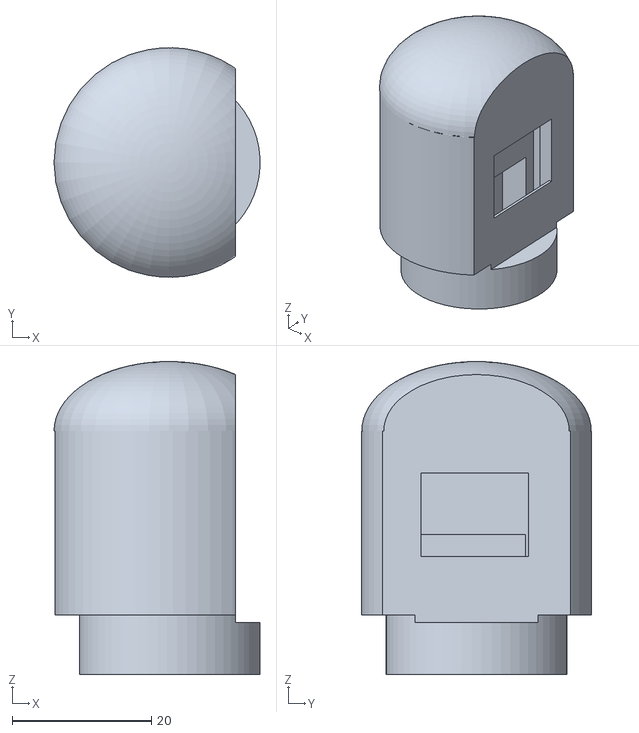
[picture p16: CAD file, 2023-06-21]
sensor/hardware/3D_print/off_the_shelf/sensorHead_v1_noPressure.stl
29.6 x 33.0 x 45.0

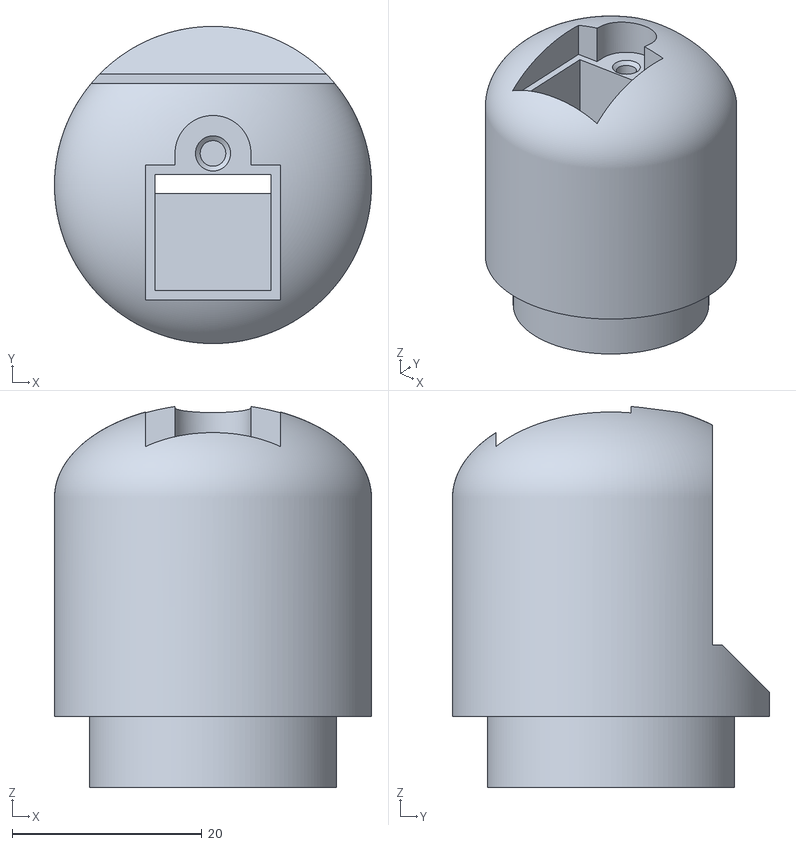
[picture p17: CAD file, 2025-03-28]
sensor/hardware/3D_print/custom_pcbs/sensor_head_m3bolt.stl
33.4 x 33.4 x 40.1

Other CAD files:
sensor/hardware/3D_print/custom_pcbs/OpenOBS_clampingCaul v10.f3z
sensor/hardware/3D_print/custom_pcbs/sensorhead_v2_filterBolt v4.f3d

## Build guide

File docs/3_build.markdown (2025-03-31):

---
layout: page
title: Build
permalink: /build/
---
## Introduction
{:.no_toc}

**This guide covers the construction of two variants of the OpenOBS:**
* **OpenOBS-328. A self contained turbidity and level sensor & logger.**
* **OpenOBS-Iridium. A bank-installed logger that can transmit data via Iridium satellite connection with a separate sensor deployed in the river.**

## Table of Contents 
{:.no_toc}
* TOC
{:toc}

## Logger Assembly

### OpenOBS-328

The logger PCBs come mostly assembled. There are just 2 parts that need to be soldered to the back side of the board.

1. Solder the QWIIC connector for the sensors. Start by adding a small dab of solder on one of the big corner pads. Let the solder solidify, and use some tweezers to grab the QWIIC connector. Remelt the solder with the iron and slide the connector in place, check that the metal legs on the back line up with the small gold pads. Solder these fine pads on the back, making sure not to short multiple pins together. If they do end up connected, try ‘swiping’ some of the solder away with a clean iron tip. If that isn’t working, then use a solder wick to remove some solder and try again. Solder the other corner pad (these give most of the mechanical strength).

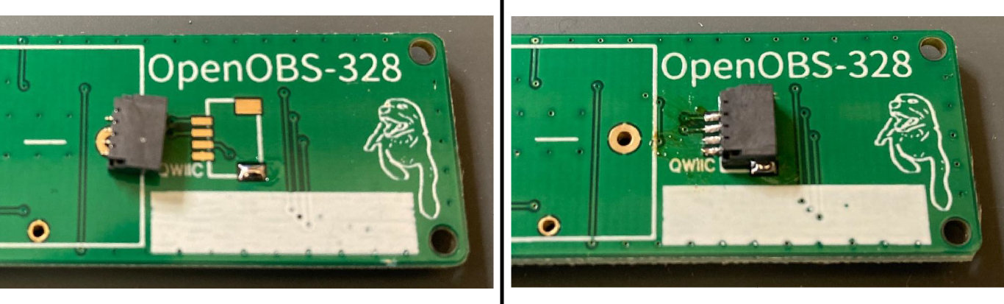
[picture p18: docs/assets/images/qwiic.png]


2. Insert the battery holder on the back. There are markings on the board and the holder for positive and negative. 

3. Flip the board over, solder the two battery holder legs, and cut off the excess.

4. Clean the residue from the solder flux around all the new joints using >90% isopropyl alcohol.

### OpenOBS-Iridium

The Iridium logger PCBs come mostly assembled. There are just 2 parts that need to be soldered to the board. 

1. Solder the WAGO wire connectors on with the levers facing towards the top of the board. 

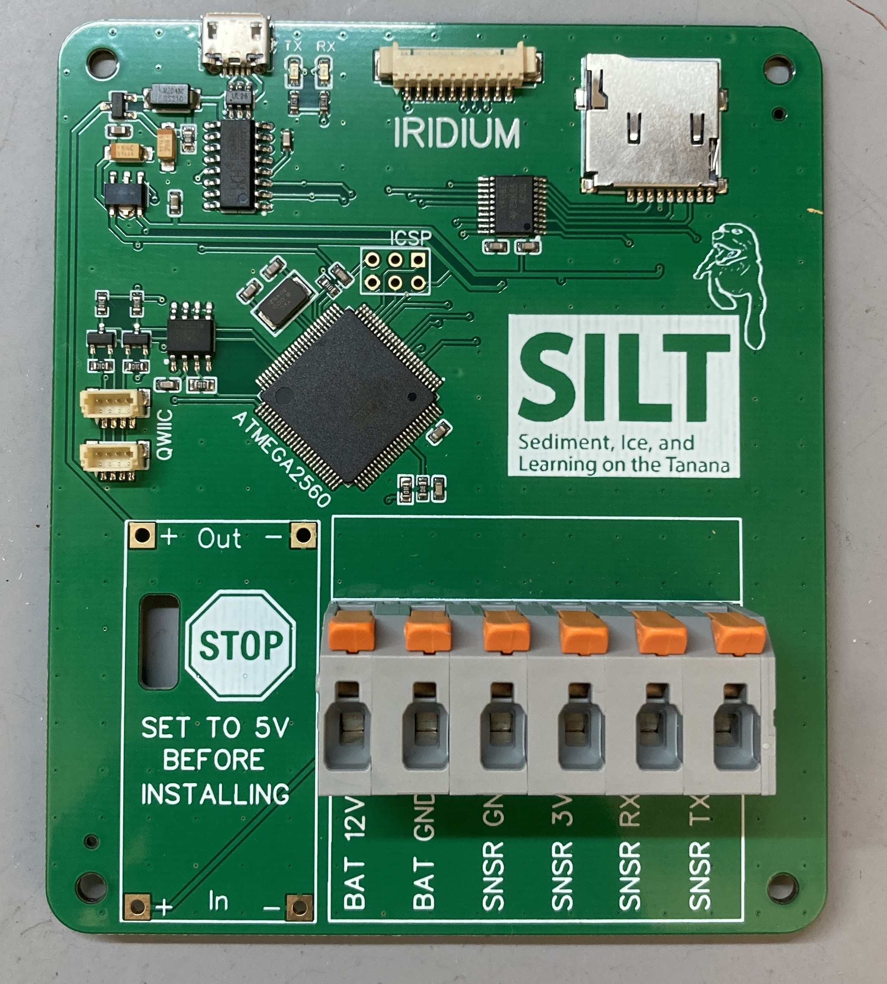
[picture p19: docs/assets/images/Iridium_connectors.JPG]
    

1. Next is the variable output buck converter for the 12V battery supply. As indicated on the PCB, we need to set the output to 5V before installing or we will let the smoke out of our electronics when we connect the battery!   
    - connect a 12V power supply or battery to the input of the buck converter using alligator clips. Measure the output with a multimeter and turn the potentiometer screw until it reads 5V +/- 0.05V. You will probably find they are set quite high from the factory and need several counter-clockwise turns before it even starts to decrease from the input voltage. 

      Bad! | Good!
      |:--:|:--:|
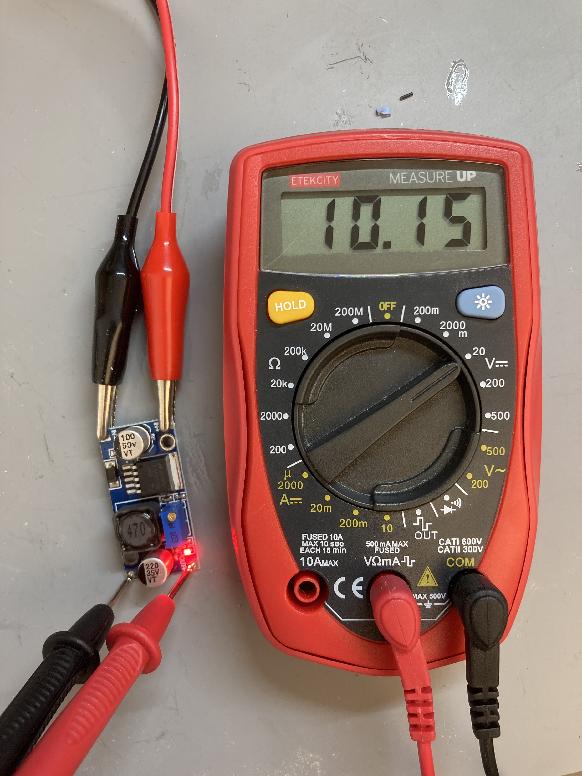
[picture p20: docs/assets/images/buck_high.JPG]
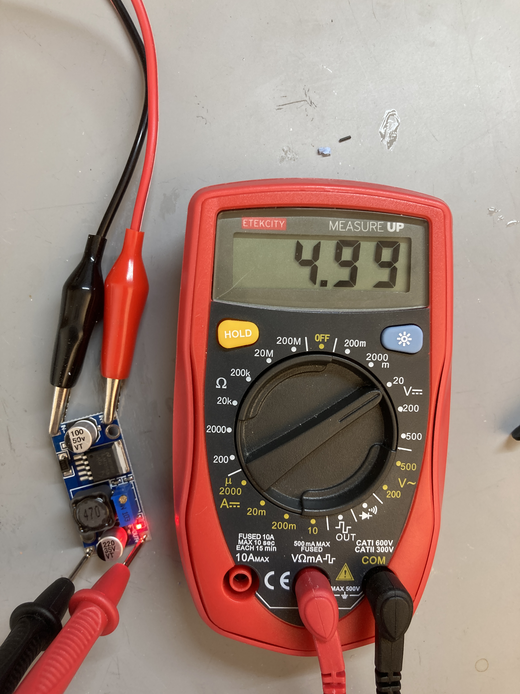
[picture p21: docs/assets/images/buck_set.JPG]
      |

    - Remove the red LED that indicates the power is on. It will only waste power when deployed and is not needed.

    - Orient the input and output of the buck converter on the PCB and solder the four corners. A bit of solid wire or old resistor leg can help transfer the heat and solder between the pads.
    - Put a big glob of hot glue over the potentiometer to keep the screw set at 5V output. 
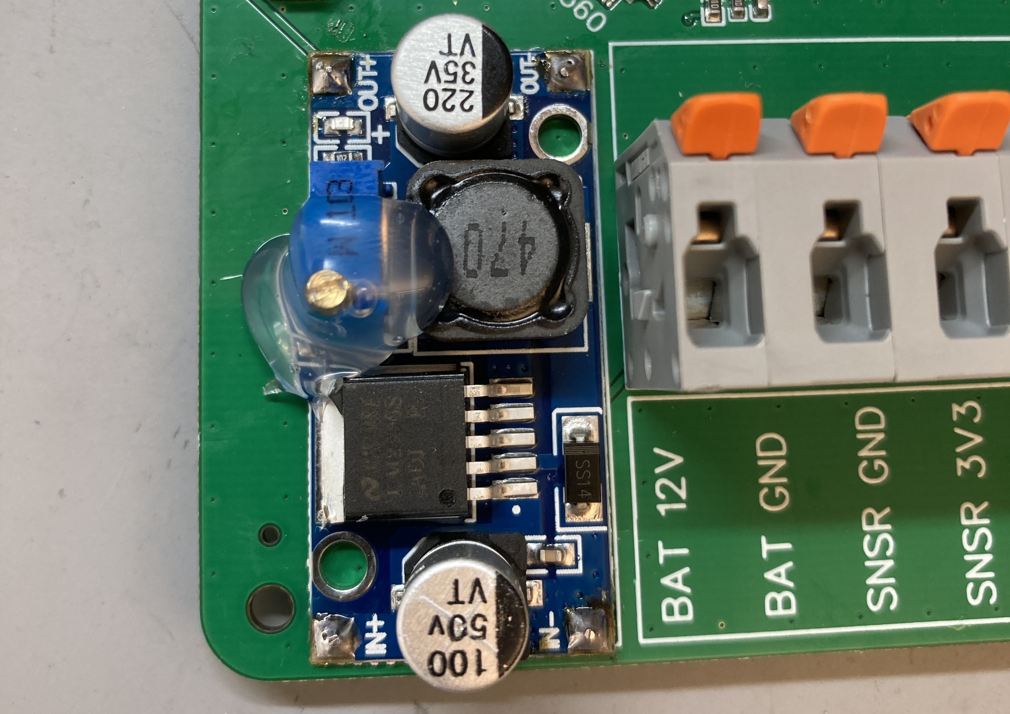
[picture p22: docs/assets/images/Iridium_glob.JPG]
      

## Sensor Head
The sensor head is one of the OpenOBS end caps, and holds the proximity sensor and the pressure sensor. The sensor head has two chambers which are filled with clear epoxy. The epoxy makes the end cap watertight, and also allows light to travel between the proximity/turbidity sensor and the water.

### 3D printing housing

The sensor housing is produced by 3D printing. [**files located here**](https://github.com/tedlanghorst/OpenOBS-328/tree/main/sensor/hardware/3D_print/custom_pcbs).  

Upload the .3mf file to the 3D printer’s interface and slice the file into machine code that can be printed. Printing settings will vary depending on your printer and materials. Here are the settings I use with a Prusa MK3S+ printer, the PrusaSlicer, and PETG filament:

* 0.2mm layer height
* 5 perimeters (greatly increases strength)
* External perimeters print first (better dimensional accuracy)
* Supports on the external overhangs only (internal overhangs can be bridged)

There is also a cap/filter for the pressure sensor to keep debris and sediment off the delicate white gel membrane. 

### Wiring
#### Pressure sensor

1. Squeeze some solder paste on the pads of the SMD adapter board. The right amount of paste is more important than keeping the paste separate on each pad. The surface tension of the melted solder should ‘snap’ the puddles of solder onto the pads.
1. Place the pressure sensor on the adapter board. Make sure the orientation is correct- there is a dot in one corner of both the adapter and the sensor that indicates orientation.
1. Use a hot air gun at 250°C to heat both sides of the sensor and completely melt the solder. The paste is a mixture of solder balls and flux. You’ll see the flux move and smoke first but keep heating to melt the solder. Aim at one side and periodically rotate the board or move the hot air gun to avoid blowing hot air directly at the white gel cap. Sometimes the hot air pushes the sensor around; check that it is still in position before removing the heat.
1. Flip the pressure sensor over to add a 100 nF capacitor and select the I2C address 0x76. 

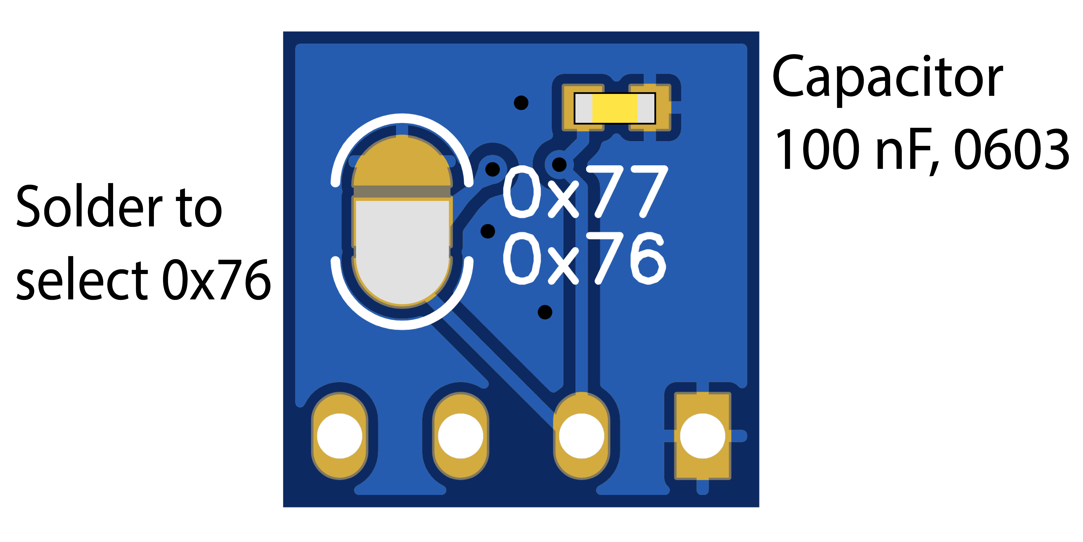
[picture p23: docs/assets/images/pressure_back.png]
    

1. Solder the 4 pin flat flex cable in from the back of the PCB.

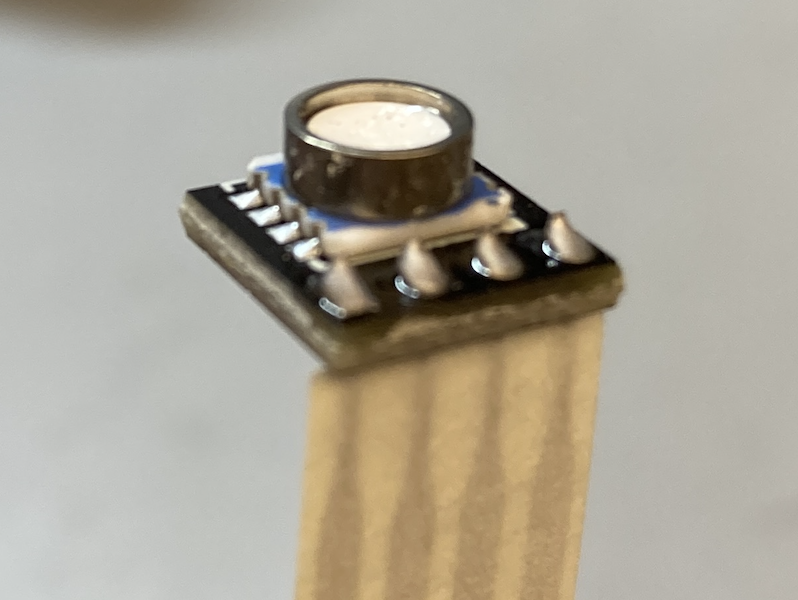
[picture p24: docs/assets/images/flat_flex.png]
    

#### Turbidity sensor

1. These steps are the same for both the OpenOBS-328 and the OpenOBS-Iridium except for this first step.
    - **OpenOBS-328:** cut one of the 50 cm QWIIC cables in half (or use the other half from last time).
    - **OpenOBS-Iridium:** cut another set of 6 cm long, 30 AWG wires in red, black, blue, and yellow.
1. Separate the four strands and strip their ends.
1. Put the pressure sensor assembly in the 3D printed sensor head 
1. Solder the pressure sensor and turbidity sensor together using the set of 4 holes closer to the turbdity sensor. Make sure the orientation is correct so that the turbidity sensor slides into the housing facing out.

    <p align="center">
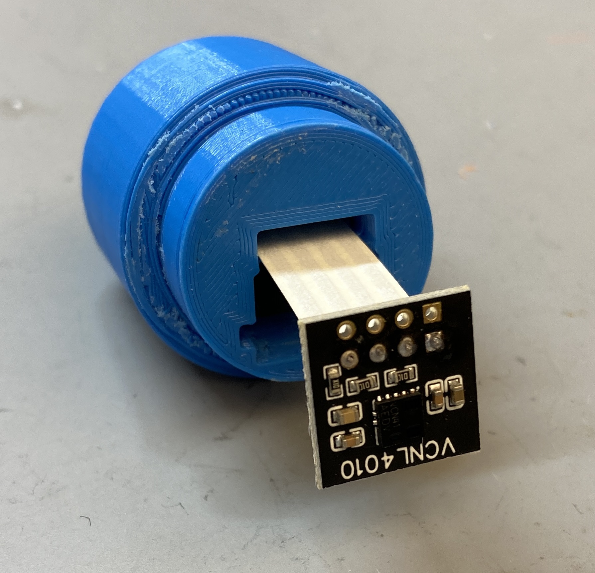
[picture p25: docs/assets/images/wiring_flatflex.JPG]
      
    </p>

1. Solder the QWIIC cable on to the other set of 4 holes towards the edge of the turbidity sensor.

    <table>
    <thead>
      <tr>
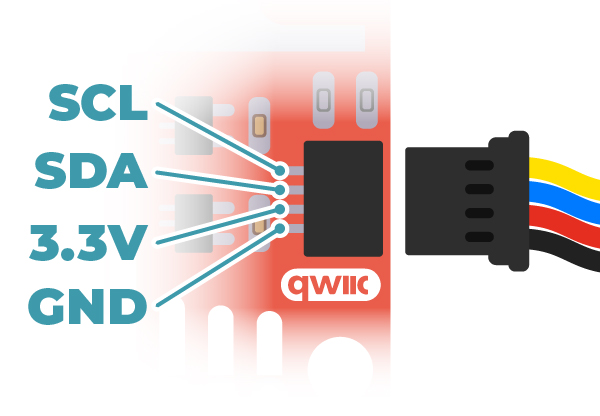
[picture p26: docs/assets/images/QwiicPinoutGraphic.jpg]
        <td rowspan="4"> </td>
        <td><b><font color="yellow">SCL</font></b></td>
        <td>yellow</td>
      </tr>
      <tr>
        <td><b><font color="blue">SDA</font></b></td>
        <td>blue</td>
      </tr>
      <tr>
        <td><b><font color="red">3V3 </font></b></td>
        <td>red</td>
      </tr>
      <tr>
        <td><b><font color="black">GND</font></b></td>
        <td>black</td>
      </tr>
    </thead>
    </table>

    *Image from [Sparkfun](https://www.sparkfun.com/qwiic)*

1. Slide the proximity sensor into the head by pushing on the end of the PCB with a long flat tool. A scrap of protoboard works really well. It might take some force to get it all the way down, and if the tool slips off the PCB it’s very possible to break the wires you just soldered on.
1. Finally, test the connections. If you are building an OpenOBS-328, you can simply plug the connector into one of the logger PCBs. If you have built the sensor with short bare wires for the OpenOBS-Iridium you can use alligator clips to connect to a test board. This is your last chance to fix anything before potting it in epoxy! 
    >❓ If you don’t know how to check that the sensor is working, go to the [programming section](#usb) that covers uploading code to the logger and opening the serial monitor to read its output. Once you have a working logger you can just plug in each new sensor. If the logger starts up correctly and starts printing reasonable data you are good to continue! 

### Epoxy potting
#### Turbidity sensor
1. The sensor head needs to be situated upside down in order to pour the epoxy. Place a shiny silicone pad or tuck tape (tyvek sheathing tape) between the sensor head and a flat surface (a granite countertop sample works well). The epoxy will not stick to the silicone pad and leaves a smooth surface. 
1. Clamp or tape the sensor head securely to the slab. If you are doing more than a few sensors, I recommend printing [this clamping caul](https://github.com/tedlanghorst/OpenOBS-328/tree/main/sensor/hardware/3D_print/custom_pcbs/clampingCaul_v2_5x.3mf) that securely holdes 5 sensors at a time. If your printer does not have tight tolerances, you may have to increase the size slightly, there is only 0.2mm clearance. 

    <p align="center">
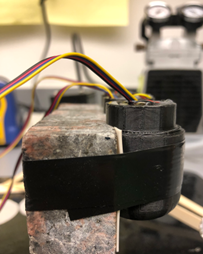
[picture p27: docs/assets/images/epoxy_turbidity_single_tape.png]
      
    </p>
    
    *Single sensor taped to a granite block. Stretching electrical tape gives enough pressure to stop leaks.*

    <br>
    
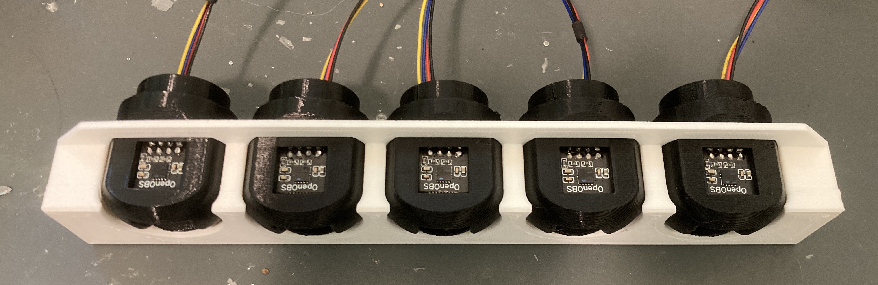
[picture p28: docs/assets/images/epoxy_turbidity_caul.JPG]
    
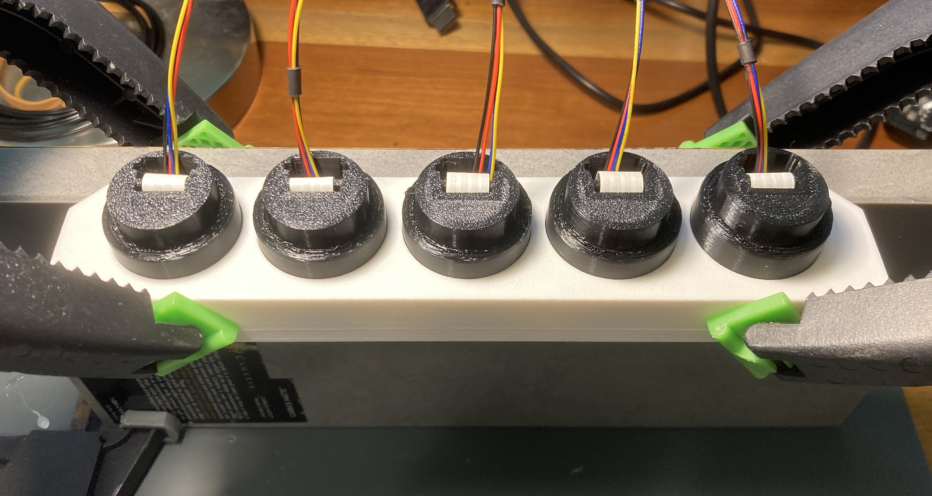
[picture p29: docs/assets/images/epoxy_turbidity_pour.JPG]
    
    *3D printed clamping caul. This required a 3rd clamp in the middle to stop leaks.*

1. Prepare the epoxy by weighing out two parts Vivid Scientific Epoxy 128 (red label) and one part Epoxy 762 (green label) in a silicone or disposable weighing dish. One turbidity sensor requires only about 2 g Epoxy 128 and 1 g Epoxy 762. Thoroughly mix the two parts to ensure it cures fully.

1. At this stage, the epoxy will contain bubbles, which will interfere with the optical path of the proximity sensor. Remove the bubbles by alternating between these two methods 2-3x until the epoxy is clear:
    - **Vacuum chamber** expands bubbles and brings them to the surface. 

    - **Heat gun** reduces the viscosity of the epoxy, allowing bubbles to rise to the surface and burst. 
      >⚠️ Although the heat setting for soldering purposes is 250 ℃, the heat gun should be set to ~120 ℃ when working with the epoxy. Too much heat will make the epoxy set rapidly.

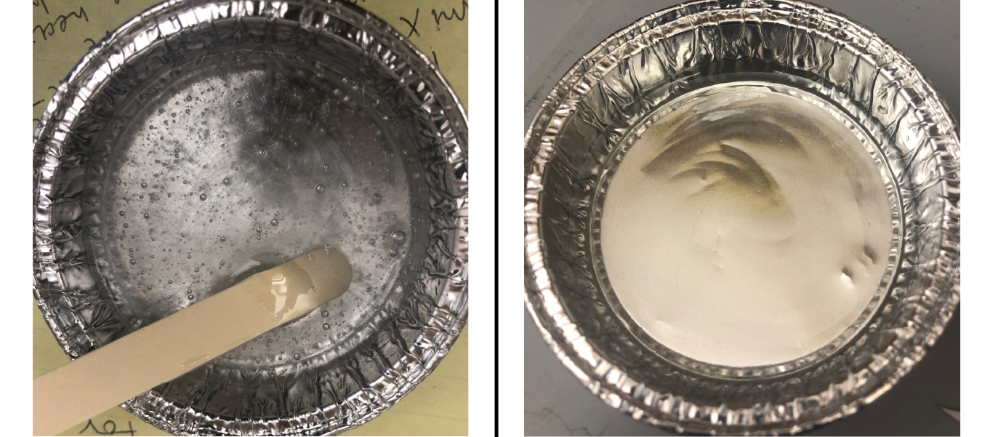
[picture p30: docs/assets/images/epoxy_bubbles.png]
    
    *Epoxy just after mixing (left) and after the vacuum/heat process (right)*

1. Once the epoxy is bubble free, slowly pour it into the proximity sensor slot. The level of the epoxy should go above the proximity sensor window but below the opening for the pressure sensor- we don't want epoxy dripping down on to the pressure sensor in this orientation. Allow the epoxy to cure for 12-24 hours before unclamping/removing tape.

    <p align="center">
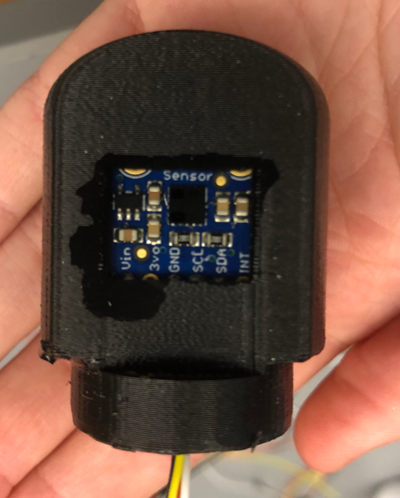
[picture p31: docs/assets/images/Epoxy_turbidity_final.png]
      
    </p>
    
    *Face of the turbidity sensor after curing (older version but similar).*

#### Pressure sensor
1. Use hot glue to seal the hole at the base of the pressure sensor slot. This will keep the epoxy from leaking down.
    <p align="center">
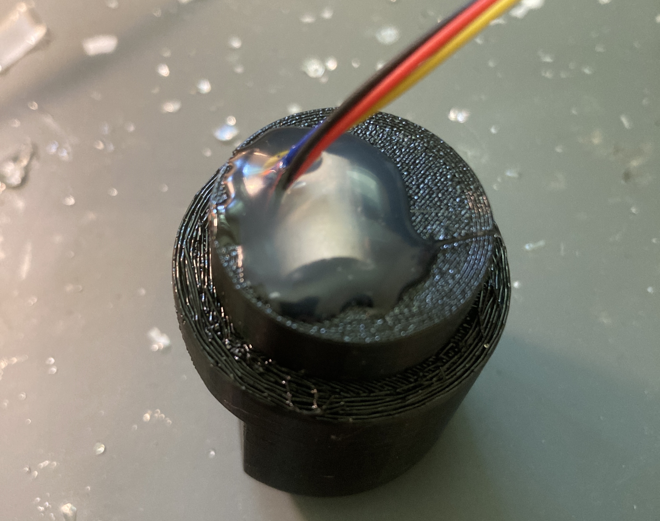
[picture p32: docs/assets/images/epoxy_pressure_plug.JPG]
      
    </p>

1. Set the sensor head upright so that the pressure sensor is facing up.
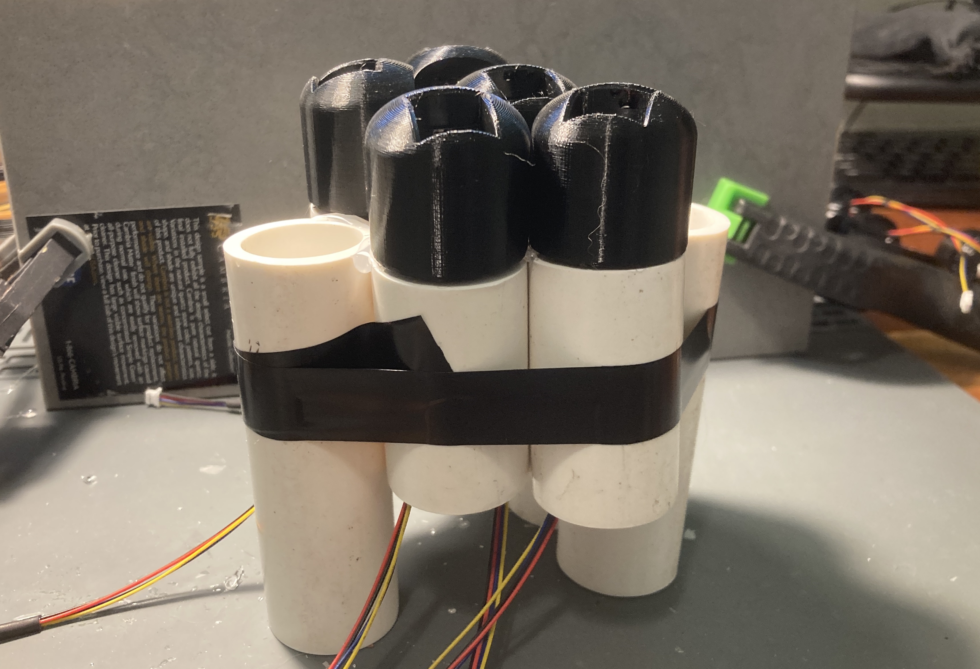
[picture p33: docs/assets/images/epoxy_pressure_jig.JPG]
    
    *A quick jig using scrap PVC to hold the sensor heads upright.*

1. Prepare epoxy as in the previous section. Again, one sensor requires about 2g Epoxy 128 and 1g Epoxy 762.
1. Once the epoxy is bubble free, use a disposable pipette to fill the pressure sensor opening to a level that **covers the electronics but without getting epoxy on the white gel membrane of the pressure sensor**. Allow the epoxy to cure for 12-24 hours again.

    

## Final Assembly
1. Cut a 6" length of 1” diameter PVC. Wash it now if necessary.
1. In a well ventilated space (e.g. fume hood, fan in a window, outdoors), attach the completed sensor head to the PVC using PVC cement. Apply the cement all around the small diameter of the sensor head and then insert. Twist to spread the cement.
1. Allow the cement to dry for about 30 mins (or according to the instructions on the can). 
1. Flip the sensor housing so the open end is up and pour about 10g of mixed epoxy inside the housing, down on the inside of the sensor head. This will prevent leaks at the junction of the sensor head with the PVC better than the PVC cement alone.


*Version 1 of the sensor head pictured. This photo does not include the PVC cement or epoxy that would seal the sensor head in place.*

## Programming 
### ISP & Bootloading

When we order new PCBs with microcontrollers on them, they are a blank slate with default configurations and no code running. The bootloader is firmware that we ‘burn’ on the microcontroller that defines some settings and subsequently allows us to upload Arduino code via the USB connection. You can think of this kind of like the BIOS of a regular computer: it doesn’t do much on its own, but it lets us install an operating system and then run programs etc. Because this step sets up the protocol for uploading from USB, we have to send this firmware to the microcontroller through the In System Programming (ISP) connections before we can use the USB connection on the OpenOBS-328.

You can find additional background info [here](https://linuxhint.com/bootloader-arduino/) if you want to read more!

#### *ISP programmer*
We will use an Arduino Nano that already has a bootloader installed to burn our new device. It will be a lot easier if you find an Arduino Nano that does not have the header pins already soldered in place. In addition to the 6 pogo pin connectors, you will need to attach a wire from pin D10 to the RST pogo and then cut (scratch out) the RST trace on the Nano. The capacitor between ground and reset in the image below can help with stability, but is not always necessary. 

Next, make sure the correct board (Arduino Nano) is selected in the IDE (Tools -> Board) and then upload the ArduinoISP sketch (File -> Examples -> ArduinoISP).

D10 wire | D10 to RST | RST trace cut
|:------:|:----------:|:-----------:|
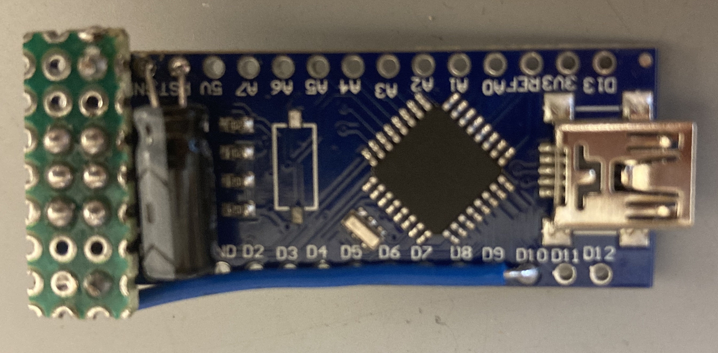
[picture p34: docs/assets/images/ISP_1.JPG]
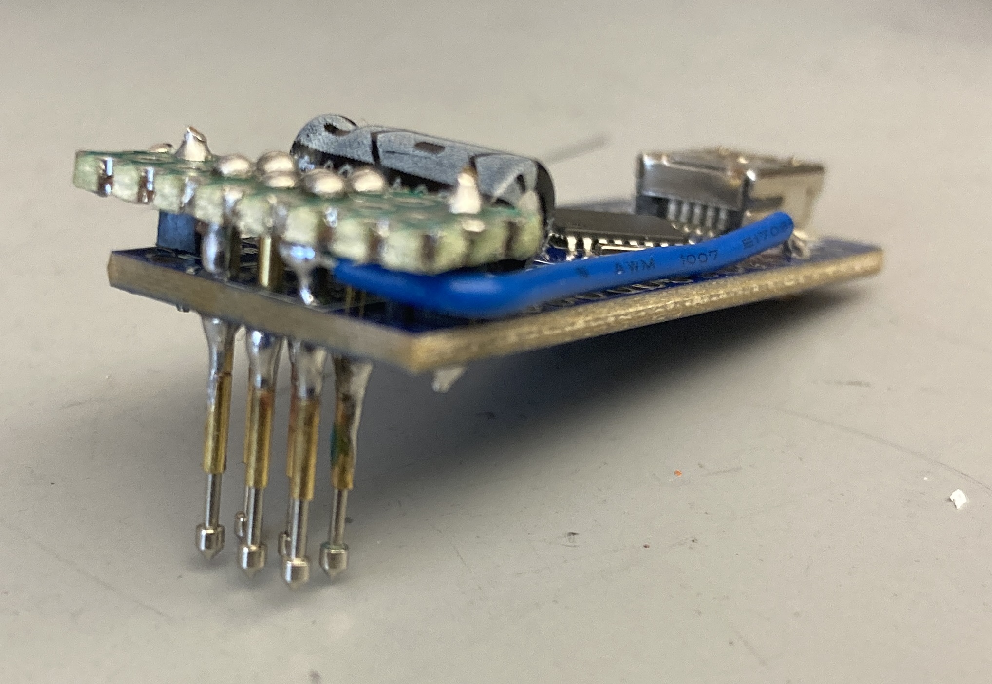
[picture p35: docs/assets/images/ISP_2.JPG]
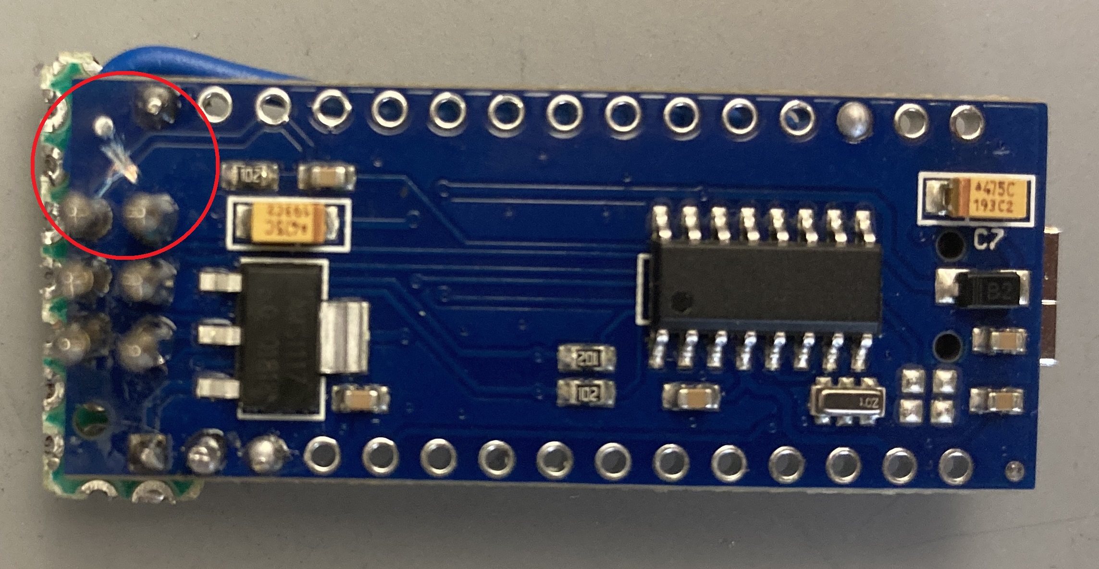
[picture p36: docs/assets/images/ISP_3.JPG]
||

#### *Connections*
The OpenOBS boards all use the standard AVR ISP 2x3 grid so we can use the customized Arduino Nano from above directly on the pads. The corner holes will help locate the pins, but be careful not to twist too much and break the pins.

>⚠️ Never connect the powered ISP programmer to the board while the sensor head is attached. The programmer works at 5V, while the sensor heads are only rated to ~4V max. It likely will not immediately break the sensors but could do damage that will make them less reliable in the future.

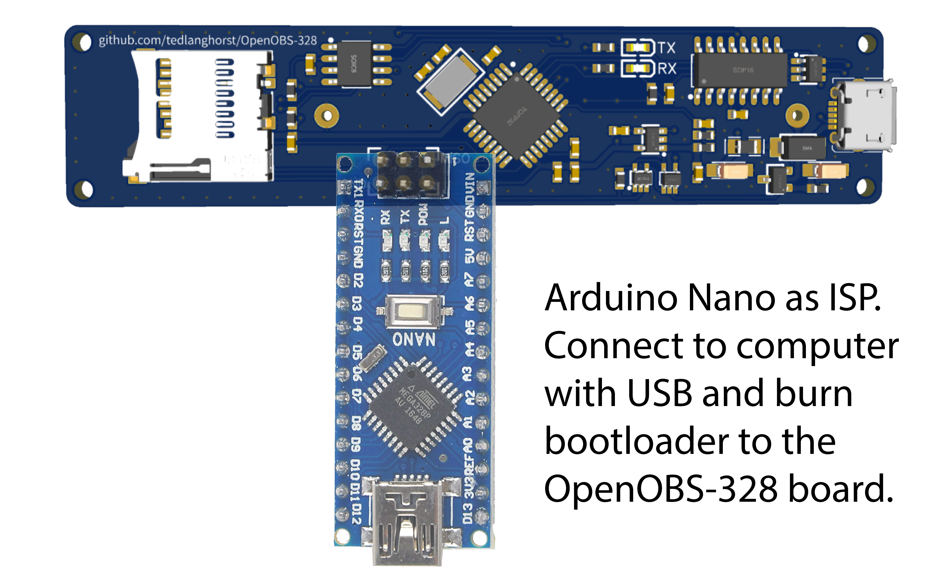
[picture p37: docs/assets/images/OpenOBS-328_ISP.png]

*Orientation of the Arduino Nano ISP and the OpenOBS-328*

#### *Board options* 
We have a custom circuit and the standard Arduino board options will not work for us. The next section covers how to add new, custom options to the Arduino IDE. 

We will use the [MiniCore](https://github.com/MCUdude/MiniCore) and [MegaCore](https://github.com/MCUdude/MegaCore) set of boards for our custom circuits. See the instructions for both under “Board Manager Installation” at the following links for how to make these options available in the Arduino IDE ([minicore install link](https://github.com/MCUdude/MiniCore#how-to-install); [megacore install link](https://github.com/MCUdude/MegaCore#how-to-install))

Once you have installed the new boards options, you can click on Tools -> Boards -> MiniCore -> ATmega328 (for OpenOBS-328 and the OpenOBS-Iridium sensor) or Tools -> Boards -> MegaCore -> ATmega2560 (for the OpenOBS-Iridium logger) from the top menu. Now, under tools -> boards there will be many new options for our microcontroller. Use the following settings whenever burning the bootloader  ***or*** uploading new sketches:

**Table 1: Board settings for uploading to OpenOBS devices.**

<style type="text/css">
.tg  {border-collapse:collapse;border-spacing:0;}
.tg td{border-color:black;border-style:solid;border-width:1px;font-family:Arial, sans-serif;font-size:14px;
  overflow:hidden;padding:10px 5px;word-break:normal;}
.tg th{border-color:black;border-style:solid;border-width:1px;font-family:Arial, sans-serif;font-size:14px;
  font-weight:normal;overflow:hidden;padding:10px 5px;word-break:normal;}
.tg .tg-c3ow{border-color:inherit;text-align:center;vertical-align:top}
.tg .tg-0pky{border-color:inherit;text-align:left;vertical-align:top}
.tg .tg-fymr{border-color:inherit;font-weight:bold;text-align:left;vertical-align:top}
</style>
<table class="tg">
<thead>
  <tr>
    <th class="tg-0pky"><span style="font-weight:700;font-style:normal;text-decoration:none;color:#000;background-color:transparent"></span></th>
    <th class="tg-c3ow"><span style="font-weight:700;font-style:normal;text-decoration:none;color:#000;background-color:transparent">OpenOBS-328</span></th>
    <th class="tg-c3ow"><span style="font-weight:700;font-style:normal;text-decoration:none;color:#000;background-color:transparent">OpenOBS-Iridium Sensor</span></th>
    <th class="tg-c3ow"><span style="font-weight:700;font-style:normal;text-decoration:none;color:#000;background-color:transparent">OpenOBS-Iridium Logger</span></th>
  </tr>
</thead>
<tbody>
  <tr>
    <td class="tg-fymr"><span style="font-style:normal;text-decoration:none;color:#000;background-color:transparent">Board</span></td>
    <td class="tg-c3ow"><span style="font-weight:400;font-style:normal;text-decoration:none;color:#000;background-color:transparent">MiniCore -&gt; ATmega328</span></td>
    <td class="tg-c3ow"><span style="font-weight:400;font-style:normal;text-decoration:none;color:#000;background-color:transparent">MiniCore -&gt; ATmega328</span></td>
    <td class="tg-c3ow"><span style="font-weight:400;font-style:normal;text-decoration:none;color:#000;background-color:transparent">MegaCore -&gt; ATmega2560</span></td>
  </tr>
  <tr>
    <td class="tg-fymr"><span style="font-style:normal;text-decoration:none;color:#000;background-color:transparent">Clock</span></td>
    <td class="tg-c3ow" colspan="3"><span style="font-weight:400;font-style:normal;text-decoration:none;color:#000;background-color:transparent">External 8MHz</span></td>
  </tr>
  <tr>
    <td class="tg-fymr"><span style="font-style:normal;text-decoration:none;color:#000;background-color:transparent">BOD</span></td>
    <td class="tg-c3ow"><span style="font-weight:400;font-style:normal;text-decoration:none;color:#000;background-color:transparent">2.7V</span></td>
    <td class="tg-c3ow"><span style="font-weight:400;font-style:normal;text-decoration:none;color:#000;background-color:transparent">2.7V</span></td>
    <td class="tg-c3ow"><span style="font-weight:400;font-style:normal;text-decoration:none;color:#000;background-color:transparent">4.3V</span></td>
  </tr>
  <tr>
    <td class="tg-fymr"><span style="font-style:normal;text-decoration:none;color:#000;background-color:transparent">EEPROM</span></td>
    <td class="tg-c3ow" colspan="3"><span style="font-weight:400;font-style:normal;text-decoration:none;color:#000;background-color:transparent">EEPROM retained</span></td>
  </tr>
  <tr>
    <td class="tg-fymr"><span style="font-style:normal;text-decoration:none;color:#000;background-color:transparent">Compiler LTO</span></td>
    <td class="tg-c3ow" colspan="3"><span style="font-weight:400;font-style:normal;text-decoration:none;color:#000;background-color:transparent">LTO enabled</span></td>
  </tr>
  <tr>
    <td class="tg-fymr"><span style="font-style:normal;text-decoration:none;color:#000;background-color:transparent">Variant</span></td>
    <td class="tg-c3ow"><span style="font-weight:400;font-style:normal;text-decoration:none;color:#000;background-color:transparent">328P/328PA</span></td>
    <td class="tg-c3ow"><span style="font-weight:400;font-style:normal;text-decoration:none;color:#000;background-color:transparent">328P/328PA</span></td>
    <td class="tg-c3ow"><span style="font-weight:400;font-style:normal;text-decoration:none;color:#000;background-color:transparent">N/A</span></td>
  </tr>
  <tr>
    <td class="tg-fymr"><span style="font-style:normal;text-decoration:none;color:#000;background-color:transparent">Pinout</span></td>
    <td class="tg-c3ow"><span style="font-weight:400;font-style:normal;text-decoration:none;color:#000;background-color:transparent">N/A</span></td>
    <td class="tg-c3ow"><span style="font-weight:400;font-style:normal;text-decoration:none;color:#000;background-color:transparent">N/A</span></td>
    <td class="tg-c3ow"><span style="font-weight:400;font-style:normal;text-decoration:none;color:#000;background-color:transparent">Arduino MEGA pinout</span></td>
  </tr>
  <tr>
    <td class="tg-fymr"><span style="font-style:normal;text-decoration:none;color:#000;background-color:transparent">Bootloader</span></td>
    <td class="tg-c3ow"><span style="font-weight:400;font-style:normal;text-decoration:none;color:#000;background-color:transparent">Yes (UART0)</span></td>
    <td class="tg-c3ow"><span style="font-weight:400;font-style:normal;text-decoration:none;color:#000;background-color:transparent">No bootloader</span></td>
    <td class="tg-c3ow"><span style="font-weight:400;font-style:normal;text-decoration:none;color:#000;background-color:transparent">Yes (UART0)</span></td>
  </tr>
</tbody>
</table>
<br>

#### *Burning Booatloader* 
After selecting the correct board options for the OpenOBS, make sure "Arduino as ISP" is selected under Tools -> Programmer. Connect the ISP programmer pins to the OpenOBS and then go to Tools -> Burn Bootloader. Wait for a message that indicates success and then you're done! You can now upload sketches over USB.

### USB

After installing the Arduino bootloader via the ISP programming, we can now upload code via the micro-USB connection. 

#### Setup

1. If you already have the [Arduino IDE](https://www.arduino.cc/en/software) and know how to connect and upload code, skip ahead to the next step. Otherwise, download and install the free Arduino IDE and follow [this guide](https://learn.adafruit.com/ladyadas-learn-arduino-lesson-number-1/upload-your-first-sketch) to get familiar with the IDE and learn how to upload code. 

1. Review the section “Setting board options” earlier in this section and use Table 1 to pick the correct board in the Arduino IDE.
	
1. Download and unzip the entire github repo for the sensor you are working with to get the latest code and documentation.

1. The Arduino IDE comes with many libraries, and we have packaged several others with the OBS code, but one library needs to be installed separately using the Arduino Library Manager. Search for “SdFat” (by Bill Greiman) and click install. 

#### Firmware

1. Open the correct sensor firmware in the Arduino IDE 

1. Check the variables near the top of the script, right after the libraries. 

    ~~~ Arduino
    // Likely variables to change
    #define MS5803_VERSION 5 //comment or remove if you aren't using the pressure sensor
    long sleepDuration_seconds = 0; 
    const char contactInfo[] PROGMEM = "If found, please contact XXX@XXX.com";
    ~~~

    Most important right now is the MS5803_VERSION variable, which can be either be 2, 5, or 14, depending on the version of the MS5803 pressure sensor you are pairing this logger with. If you are building the device without a pressure sensor, you can remove this line. 

    >⚠️ The sensor version is really important to get right. If it is wrong, the pressure and temperature data will be very hard to recover.
  
1. Upload the sketch to the logger. Watch the IDE status bar for the code to be compiled and uploaded.
    >❓ If you can't find the COM port for the OpenOBS, you likely need to install the [CH340 USB driver](https://learn.sparkfun.com/tutorials/how-to-install-ch340-drivers/all).

1. Open the Serial Monitor (Tools -> Serial Monitor) and verify that the OpenOBS is starting up and communicating. Change the baud rate to 250000 in the bottom right corner of the Serial Monitor if it is not already set.

1. If the serial number has not been set, the serial monitor will prompt you to set it now by typing it at the top of the window. If you need to change it in the future, use the sketch titled “reset_serial_number.ino”, follow the prompts in the serial monitor, and then reupload the regular sensor firmware.

#### *Programming with ISP*
We can also send our Arduino program to the microcontroller directly through the ISP, rather than installing a bootloader and then programming through USB. The advantage to this method is that we do not need the hardware for a USB connection. **We will only use ISP programming for the sensor end of the OpenOBS-Iridium variant**, because once we verify the sensor is working, we will encase it in epoxy.

After following the bootloader instructions above, keep the ISP programmer in place and go to Sketch -> Upload Using Programmer to upload the code.

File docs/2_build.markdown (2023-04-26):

---
layout: page
title: Build
permalink: /build/
---
## Introduction
{:.no_toc}

**This guide covers the construction of two variants of the OpenOBS:**
* **OpenOBS-328. A self contained turbidity and level sensor & logger.**
* **OpenOBS-Iridium. A bank-installed logger that can transmit data via Iridium satellite connection with a separate sensor deployed in the river.**

## Table of Contents 
{:.no_toc}
* TOC
{:toc}

## Tools & Materials
* Soldering iron
* Solder
* No clean solder paste
* Hot air gun/station for electronics. (sometimes called rework station)
* Vacuum pump
* Vacuum chamber
* Hot glue gun
* 3D printer
* PVC pipe cutter
* Electronics tweezers
* Fine flush cutters
* Wire strippers (22-30 AWG)
* 30 AWG wire (red, black, blue, yellow)
* Vivid scientific epoxy
* SCIPGRIP 16 acrylic cement

## Parts
[OpenOBS-328](https://docs.google.com/spreadsheets/d/11F4owaMOkx01ESch3bgcQnwAiDcHpwIU8byPSdr5rsE/edit#gid=601615659)

[OpenOBS-Iridium](https://docs.google.com/spreadsheets/d/11F4owaMOkx01ESch3bgcQnwAiDcHpwIU8byPSdr5rsE/edit#gid=685555300)

## Programming 
These two sections provide background information for programming OpenOBS devices. In the logger assembly sections later on we will assume you understand these concepts and have set up your computer to be able to program the new device.

### ISP & Bootloading
**Introduction**
When we order new PCBs with microcontrollers on them, they are a blank slate with default configurations and no code running. The bootloader is firmware that we ‘burn’ on the microcontroller that defines some settings and subsequently allows us to upload Arduino code via the USB connection. You can think of this kind of like the BIOS of a regular computer; it doesn’t do much on its own, but it lets us install an operating system and then run programs etc. Because this step sets up the protocol for uploading from USB, we have to send this firmware to the microcontroller through the In System Programmer (ISP) connections.

You can find additional background info [here](https://linuxhint.com/bootloader-arduino/) if you want to read more!

**Connections**
You can buy specialized devices that act as an ISP, but it is easy enough to just use another Arduino that already has a bootloader installed to burn a new device. Read through [this tutorial](https://docs.arduino.cc/built-in-examples/arduino-isp/ArduinoISP) for how ISP uploading works and how to use an Arduino as the programmer. Don’t worry about all the examples they give on how to use different “programmers” and “hosts”, just understand the basic idea. We will follow the 8-step guide section at the end of the tutorial. At step 5, it says: 

Select the item in the Tools > Board menu that corresponds to the board on which you want to burn the bootloader (not the board that you're using as the programmer). See the board descriptions on the environment page for details.

We have a custom circuit and the standard Arduino board options will not work for us. The next section covers how to add new, custom options. 

**Setting board options**
We will use the [MiniCore](https://github.com/MCUdude/MiniCore) and [MegaCore](https://github.com/MCUdude/MegaCore) set of boards for our custom circuit. See the instructions for both under “Board Manager Installation” for how to make these options available in the Arduino IDE ([minicore install link](https://github.com/MCUdude/MiniCore#how-to-install); [megacore install link](https://github.com/MCUdude/MegaCore#how-to-install))

Once you’ve installed the new boards options, you can click on Tools -> Boards -> MiniCore -> ATmega328 (for OpenOBS-328 and the OpenOBS-Iridium sensor) or Tools -> Boards -> MegaCore -> ATmega2560 (for the OpenOBS-Iridium logger) from the top menu. Now, under tools -> boards there will be many new options for our microcontroller. Use the following settings whenever uploading any code:

**Table 1: Board settings for uploading to OpenOBS devices.**

<style type="text/css">
.tg  {border-collapse:collapse;border-spacing:0;}
.tg td{border-color:black;border-style:solid;border-width:1px;font-family:Arial, sans-serif;font-size:14px;
  overflow:hidden;padding:10px 5px;word-break:normal;}
.tg th{border-color:black;border-style:solid;border-width:1px;font-family:Arial, sans-serif;font-size:14px;
  font-weight:normal;overflow:hidden;padding:10px 5px;word-break:normal;}
.tg .tg-c3ow{border-color:inherit;text-align:center;vertical-align:top}
.tg .tg-0pky{border-color:inherit;text-align:left;vertical-align:top}
.tg .tg-fymr{border-color:inherit;font-weight:bold;text-align:left;vertical-align:top}
</style>
<table class="tg">
<thead>
  <tr>
    <th class="tg-0pky"><span style="font-weight:700;font-style:normal;text-decoration:none;color:#000;background-color:transparent">OpenOBS variants</span></th>
    <th class="tg-c3ow"><span style="font-weight:700;font-style:normal;text-decoration:none;color:#000;background-color:transparent">OpenOBS-328</span></th>
    <th class="tg-c3ow"><span style="font-weight:700;font-style:normal;text-decoration:none;color:#000;background-color:transparent">OpenOBS-Iridium Sensor</span></th>
    <th class="tg-c3ow"><span style="font-weight:700;font-style:normal;text-decoration:none;color:#000;background-color:transparent">OpenOBS-Iridium Logger</span></th>
  </tr>
</thead>
<tbody>
  <tr>
    <td class="tg-fymr"><span style="font-style:normal;text-decoration:none;color:#000;background-color:transparent">Board</span></td>
    <td class="tg-c3ow"><span style="font-weight:400;font-style:normal;text-decoration:none;color:#000;background-color:transparent">MiniCore -&gt; ATmega328</span></td>
    <td class="tg-c3ow"><span style="font-weight:400;font-style:normal;text-decoration:none;color:#000;background-color:transparent">MiniCore -&gt; ATmega328</span></td>
    <td class="tg-c3ow"><span style="font-weight:400;font-style:normal;text-decoration:none;color:#000;background-color:transparent">MegaCore -&gt; ATmega2560</span></td>
  </tr>
  <tr>
    <td class="tg-fymr"><span style="font-style:normal;text-decoration:none;color:#000;background-color:transparent">Clock</span></td>
    <td class="tg-c3ow" colspan="3"><span style="font-weight:400;font-style:normal;text-decoration:none;color:#000;background-color:transparent">External 8MHz</span></td>
  </tr>
  <tr>
    <td class="tg-fymr"><span style="font-style:normal;text-decoration:none;color:#000;background-color:transparent">BOD</span></td>
    <td class="tg-c3ow"><span style="font-weight:400;font-style:normal;text-decoration:none;color:#000;background-color:transparent">2.7V</span></td>
    <td class="tg-c3ow"><span style="font-weight:400;font-style:normal;text-decoration:none;color:#000;background-color:transparent">2.7V</span></td>
    <td class="tg-c3ow"><span style="font-weight:400;font-style:normal;text-decoration:none;color:#000;background-color:transparent">4.3V</span></td>
  </tr>
  <tr>
    <td class="tg-fymr"><span style="font-style:normal;text-decoration:none;color:#000;background-color:transparent">EEPROM</span></td>
    <td class="tg-c3ow" colspan="3"><span style="font-weight:400;font-style:normal;text-decoration:none;color:#000;background-color:transparent">EEPROM retained</span></td>
  </tr>
  <tr>
    <td class="tg-fymr"><span style="font-style:normal;text-decoration:none;color:#000;background-color:transparent">Compiler LTO</span></td>
    <td class="tg-c3ow" colspan="3"><span style="font-weight:400;font-style:normal;text-decoration:none;color:#000;background-color:transparent">LTO enabled</span></td>
  </tr>
  <tr>
    <td class="tg-fymr"><span style="font-style:normal;text-decoration:none;color:#000;background-color:transparent">Variant</span></td>
    <td class="tg-c3ow"><span style="font-weight:400;font-style:normal;text-decoration:none;color:#000;background-color:transparent">328P/328PA</span></td>
    <td class="tg-c3ow"><span style="font-weight:400;font-style:normal;text-decoration:none;color:#000;background-color:transparent">328P/328PA</span></td>
    <td class="tg-c3ow"><span style="font-weight:400;font-style:normal;text-decoration:none;color:#000;background-color:transparent">N/A</span></td>
  </tr>
  <tr>
    <td class="tg-fymr"><span style="font-style:normal;text-decoration:none;color:#000;background-color:transparent">Pinout</span></td>
    <td class="tg-c3ow"><span style="font-weight:400;font-style:normal;text-decoration:none;color:#000;background-color:transparent">N/A</span></td>
    <td class="tg-c3ow"><span style="font-weight:400;font-style:normal;text-decoration:none;color:#000;background-color:transparent">N/A</span></td>
    <td class="tg-c3ow"><span style="font-weight:400;font-style:normal;text-decoration:none;color:#000;background-color:transparent">Arduino MEGA pinout</span></td>
  </tr>
  <tr>
    <td class="tg-fymr"><span style="font-style:normal;text-decoration:none;color:#000;background-color:transparent">Bootloader</span></td>
    <td class="tg-c3ow"><span style="font-weight:400;font-style:normal;text-decoration:none;color:#000;background-color:transparent">Yes (UART0)</span></td>
    <td class="tg-c3ow"><span style="font-weight:400;font-style:normal;text-decoration:none;color:#000;background-color:transparent">No bootloader</span></td>
    <td class="tg-c3ow"><span style="font-weight:400;font-style:normal;text-decoration:none;color:#000;background-color:transparent">Yes (UART0)</span></td>
  </tr>
</tbody>
</table>

**Bootloading** 

**Programming with ISP**
We can also send our Arduino program to the microcontroller directly through the ISP, rather than installing a bootloader and then programming through USB. The advantage to this method is that we do not need the hardware for a USB connection. We will only use ISP programming for the sensor end of the OpenOBS-Iridium variant, because once we verify the sensor is working, we will encase it in epoxy.

## USB

After installing the Arduino bootloader via the ISP programming, we can now upload code via the micro-USB connection. 

1. Setup

	1.1 If you already have the [Arduino IDE](https://www.arduino.cc/en/software) and know how to connect and upload code, skip ahead to the next step. Otherwise, download and install the free Arduino IDE and follow [this guide](https://learn.adafruit.com/ladyadas-learn-arduino-lesson-number-1/upload-your-first-sketch) to get familiar with the IDE and learn how to upload code. 

	1.2 Review the section “Setting board options” earlier in this section and use Table 1 to pick the correct board in the Arduino IDE.
	
	1.3 Download and unzip the entire github repo for the sensor you are working with to get the latest code and documentation.

	1.4 Libraries are chunks of code that we can import into our script and use to simplify the interactions with hardware. The Arduino IDE comes with many libraries, and we have packaged several others with the OBS code, but one library needs to be installed separately using the Arduino Library Manager. Search for “SdFat” (by Bill Greiman) and click install. 

2. Firmware

	2.1 Open the correct sensor firmware in the Arduino IDE and upload it to the OpenOBS. Watch the IDE status bar for the code to be compiled and uploaded.

	2.2 Open the Serial Monitor (Tools -> Serial Monitor) and verify that the OpenOBS is starting up and communicating. Change the baud rate to 250000 in the bottom right corner of the Serial Monitor if it is not already set.

	2.3 If the serial number has not been set, the serial monitor will prompt you to set it now by typing it at the top of the window. If you need to change it in the future, use the .ino script titled “set_serial_number.ino”, follow the prompts in the serial monitor, and then reupload the regular sensor firmware.

## Logger Assembly

### OpenOBS-328

The logger PCBs come mostly assembled. There are just 2 parts that need to be soldered to the back side of the board.

1. First, solder the QWIIC connector for the sensors. Start by adding a small dab of solder on one of the big corner pads. Let the solder solidify, and use some tweezers to grab the QWIIC connector. Remelt the solder with the iron and slide the connector in place, check that the metal legs on the back line up with the small gold pads. Solder these fine pads on the back, making sure not to short multiple pins together. If they do end up connected, try ‘swiping’ some of the solder away with a clean iron tip. If that isn’t working, then use a solder wick to remove some solder and try again. Solder the other corner pad (these give most of the mechanical strength).



2. Insert the battery holder on the back. There are markings on the board and the holder for positive and negative. 

3. Flip the board over, solder the two battery holder legs, and cut off the excess.

4. Clean the residue from the solder flux around all the new joints using >90% isopropyl alcohol.

### OpenOBS-Iridium

Work in progress...

## Sensor Head
The sensor housing is one of the OpenOBS’s end caps, and holds the proximity sensor and the pressure sensor. The housing has two chambers which are filled with clear epoxy after insertion of the sensors. The epoxy makes the end cap watertight, and also allows light to travel between the proximity sensor chip and the water.

### 3D printing housing

The sensor housing is produced by 3D printing a custom [**.stl file**](https://drive.google.com/file/d/1blsicZMW83UDPJwxpu_2UrOp7uc6YAOs/view).  

Upload the provided .stl file to the 3D printer’s interface and slice the file into machine code that can be printed.  Printing settings will vary depending on the brand of 3D printer, and certain presets like the extrusion temperature should remain at the default value. We use the following settings for Ultimaker 3 and S3 printers found at UNC:

* Add a brim. Prevents the object from sliding during printing.
* No internal support. Supports prevent overhangs (materials above a hollow space) from drooping or collapsing before the extruded material cools and hardens, but also need to be removed from the internal spaces after printing. On our printers the parts are good enough without supports, but this may not work for all printers/settings/materials etc.
* Set fill density somewhere between 50 and 100%. Reduces hollow spaces.

### Wiring
#### Pressure sensor

1. Squeeze some solder paste on the pads of the SMD adapter board. The right amount of paste is more important than keeping the paste separate on each pad. The surface tension when you melt the solder should ‘snap’ the puddles of solder onto the pads.
1. Place the pressure sensor on the adapter board. Make sure the orientation is correct- there is a dot in one corner of both the adapter and the sensor that indicates orientation.
1. Use a hot air gun at 250°C to heat both sides of the sensor and completely melt the solder. The paste is a mixture of solder and flux. You’ll see the flux melt first but keep heating to melt the solder. Aim at one side and periodically rotate the board to avoid blowing hot air directly at the white gel cap. Sometimes the hot air pushes the sensor around; check that the position is still good before removing the heat.
1. Place a 10k resistor across pins 3 and 6.
1. Place a 0.1µF (100nF) capacitor across pins 2 and 5.
1. Bend the resistor leg on pin 6 around to touch pin 5 as well. We want these to be connected after we solder (see photos/diagram below). 
1. Cut 6 cm lengths of red, black, blue, and yellow 30 AWG wire.
1. Solder the wires in place as shown below. The wires should come in from the back and hang down straight-ish at this point. Trim the wires and resistor/capacitor legs so they are well below the top of the sensor. These need to be fully covered in epoxy.
1. A bit of heat shrink on the wires below the adapter board keeps things tidy, but not necessary.

#### Turbidity sensor

1. These steps are the same for both the OpenOBS-328 and the OpenOBS-Iridium except for the first step.
    - **OpenOBS-328:** cut one of the 50 cm QWIIC cables in half (or use the other half from last time; the point here is to have a set of wires with a connector on one end and bare wires on the other).
    - **OpenOBS-Iridium:** cut another set of 4, 6 cm long, 30 AWG wires in red, black, blue, and yellow.
1. Separate the four strands and strip their ends. Strip the ends of the pressure sensor wires now too.
1. Put the pressure sensor assembly in the 3d printed sensor head 
1. Twist the matching colors together from one end of each new wire and the free end of the pressure sensor wires. Solder them in place on the proximity sensor. Bring the wires in from the back. I found it easiest to twist one pair, solder it, and then repeat with the next pair. Match the wire colors to the right solder point on the proximity sensor using this table:

	| Color  | Signal |
	|--------|--------|
	| Red    | Vin    |
	| Black  | GND    |
	| Yellow | SCL    |
	| Blue   | SDA    |

1. Slide the proximity sensor into the head by pushing on the end of the PCB with a skinny tool. A scrap of protoboard works really well. It will take some force to get it all the way down, and if the tool slips off the PCB, it’s very possible to break the wires you just soldered on.
1. Finally, test the connections. If you are building an OpenOBS-328, you can simply plug the connector into one of the logger PCBs. If you have built the sensor with shore bare wires for the OpenOBS-Iridium you can use alligator clips to connect to a test board. This is your last chance to fix anything before potting it in epoxy! 
    >If you don’t know how to check that the sensor is working, go to the [programming section](./2_build.markdown#usb) that covers uploading code to the logger and opening the serial monitor to read its output. Once you have a working logger you can just open the serial monitor for each new sensor. If the logger starts up correctly and does not write out “PTINIT,0”, or “TURBINIT,0” or similar- you are good! 
1. Use hot glue to plug up the hole at the base of the pressure sensor slot.

### Epoxy potting
#### Turbidity sensor

1. The sensor head needs to be situated with the flat side (front) facing down in order to pour the epoxy. Place a silicon pad (shiny side toward the sensor) between the sensor head and a mobile flat surface (like a slab of stone). The epoxy will not stick to the silicone pad and leaves a smooth surface. Clamp or tape securely to the slab, then maneuver the slab so the bottom of the sensor head is facing up and you can pour epoxy into the proximity sensor slot. 
1. Prepare the epoxy by weighing out two parts Vivid Scientific Epoxy 128 (red label) and one part Epoxy 762 (green label) in an aluminum weighing dish. 12 g Epoxy 128 and 6 g Epoxy 762 are enough to fill 3 proximity sensor slots. Use a popsicle stick to gently combine the two epoxies.
1. At this stage, the epoxy will contain bubbles, which will interfere with the passage of light to and from the proximity sensor. The bubbles are removed by two methods. Alternate between these two methods 2-3x until the epoxy is bubble-free.

	**Vacuum chamber:** Expands bubbles and brings them to the surface. 

	**Heat gun:** Reduces the viscosity of the epoxy, allowing bubbles to rise to the surface and burst. Note: Although the heat setting for soldering purposes is 250 ℃, the heat gun should be set to ~120 ℃ when working with the epoxy. Too much heat will make the epoxy set rapidly.

  

1. Once the epoxy is bubble free, pour slowly into the proximity sensor slot until epoxy reaches the brim. Take care that epoxy gets between the chip and the silicone pad. Allow the epoxy to cure for 24 hours before unclamping/removing tape.

#### Pressure sensor

1. Clamp or tape the sensor head securely to a slab so the top of the sensor head is facing up (hot glue facing down).
1. Add heat shrink to protect PS from epoxy
1. Prepare epoxy as before. 12 g Epoxy 128 and 6 g Epoxy 762 are enough to fill 3 pressure sensor slots. 
1. Once the epoxy is bubble free, pour slowly into the pressure sensor slot until epoxy reaches the brim of the heatshrink. Remove the heat shrink so it won't set into the epoxy, but take care not to drip epoxy onto the white circle. Allow the epoxy to cure for 24 hours before unclamping/removing tape. After curing, the sensor head is complete.

## Final Assembly
1. Cut 15cm of 1”- diameter PVC.
1. In a well ventilated space (i.e. fume hood), attach the completed sensor head to the PVC using SCIGRIP 16 Fast Set Clear Medium Bodied Solvent Cement. Apply to all points of contact between the endcap and the PVC to ensure a watertight seal. Allow the adhesive to cure for 24 hours.
1. Epoxy inside the PVC to prevent leaks at the junction of the sensor head with the PVC.

---
Lillian Cooper and Ted Langhorst.

Updated 3/18/2023

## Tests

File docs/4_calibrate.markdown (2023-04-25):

---
layout: page
title: Calibrate
permalink: /calibrate/
---

## Turbidity calibration
We do a 5 point calibration with tap water for 0 NTUs and Formazin dilutions at 100, 250, 500, and 1000 NTUs. Set the logger to run in [continuous mode](./4_deploy.markdown#deploying) (~1.1 Hz sampling) and hold it in a beaker of each NTU standard for ~30 seconds. If you're comfortable with Matlab and have a license, try the [auto-calibration script](https://github.com/tedlanghorst/OpenOBS-328/blob/main/scripts/calibrateOOBS.m) to process the data. 

## Sediment calibration

### In the field
While the logger is installed on site, visit it regularly and collect measurements of total suspended solids or suspended sediment concentration. Ideally your measurements will cover nearly the full range of values you expect to observe with the sensor. sample the sensor data when the in-situ measurements were made to calibrate the sensor response.

### In the lab
This is a hybrid of the last two options. Collect some sediment from your field site (either fines from the banks or distilled from the river). Put a large pitcher of clear water on a stir plate and add sediment in steps up to your maximum concentration. Dunk the sensor in the pitcher for ~30 seconds at each step. Subsample the pitcher at each step to measure the actual concentration.

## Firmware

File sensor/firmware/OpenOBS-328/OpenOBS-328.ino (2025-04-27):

#include <Wire.h>     //standard library
#include <SPI.h>      //standard library
#include <EEPROM.h>   //standard library
#include <SdFat.h>    //tested with Version 2.0.7 //uses 908 bytes of memory
#include "src/libs/DS3231/DS3231.h"
#include "src/libs/LowPower/LowPower.h"
#include "src/OpenOBS/Sensors.h"

// Likely variables to change
static const uint8_t MS5803_VERSION = 5;

long sleepDuration_seconds = 0; 
//

//firmware data
const DateTime uploadDT = DateTime((__DATE__), (__TIME__)); //saves compile time into progmem
const char dataColumnLabels[] PROGMEM = "time,millis,ambient_light,backscatter,pressure,water_temp,battery";
uint16_t serialNumber;

//connected pins
#define pChipSelect 10              //chip select pin for SD card
#define pBatteryDivider A2

//EEPROM addresses
#define SLEEP_ADDR 0            //4 bytes. 0-3
#define SENSOR_SETTINGS_ADDR 4  //5 bytes. 4-8
#define SN_ADDR 500             //2 bytes. 500-501
#define UPLOAD_TIME_ADDR 502    //4 bytes. 502-505.

//gui communications vars
#define COMMS_TRY 3        //number of attemps for gui connection
#define MAX_CHAR 60            //max num character in messages
char messageBuffer[MAX_CHAR];       //buffer for sending and receiving comms
bool guiConnected = false;
bool newFirmware = false;

//data storage variables
struct {
  uint32_t timeSeconds;
  uint32_t timeMillis;
  uint32_t absPressure;
  uint16_t ambientLight;
  uint16_t backscatterLight;
  int16_t waterTemp;
  uint16_t batteryVoltage;
  
  void toString(char* externalBuffer) {
    sprintf(externalBuffer, "%lu,%lu,%u,%u,%lu,%i,%u",
            timeSeconds, timeMillis, ambientLight, backscatterLight,
            absPressure, waterTemp, batteryVoltage);
  }
} data; //20 bytes

//initialization variables
union {
  byte b;
  struct {
    bool sd: 1;
    bool clk: 1;
    bool turb: 1;
    bool pt: 1;
  } module;
} startup;

//time settings
long currentTime = 0;
long delayedStart_seconds = 0;
DateTime nextAlarm;
DS3231 RTC; //create RTC object

//SD vars
#define SPI_SPEED SD_SCK_MHZ(50)
char filename[] = "YYYYMMDD.TXT";
SdFat sd;
SdFile file;
bool fileIsOpen = false;

//Sensor vars
Sensors sensors = Sensors(SENSOR_SETTINGS_ADDR, MS5803_VERSION);
uint8_t measFlags = 0b00001111;
uint8_t iredCurrent = 50;

void setup() {
  Serial.begin(250000);
  Serial.setTimeout(50);
  Wire.begin();
  
  getSerialNumber();
  getDataLoggerSettings();
  checkModuleStartup();
  getSensorSettings();

  if (delayedStart_seconds > 0) {
    sensorSleep(RTC.now().unixtime(), delayedStart_seconds);
  }
  
  updateFilename();
}


void loop()
{   
  // Put new data into the data struct.
  data.timeSeconds = RTC.now().unixtime();
  data.timeMillis = millis();
  data.batteryVoltage = analogRead(pBatteryDivider);
  sensors.getReadings(
    data.ambientLight, 
    data.backscatterLight, 
    data.absPressure, 
    data.waterTemp);

  data.toString(messageBuffer);
  writeToSD(messageBuffer);
  serialSend(messageBuffer);
  
  if (sleepDuration_seconds>0) {
    sensorSleep(data.timeSeconds, sleepDuration_seconds);
  }
  
}

void getSerialNumber(){
  EEPROM.get(SN_ADDR, serialNumber);
  //Check if SN has been changed from the default 0xFFFF.
  //If it has not, then loop through asking for a new one.
  while (serialNumber == 0xFFFF || serialNumber == 0){
    Serial.println(F("Missing serial number. Enter a valid SN [1-65534]:"));
    while(Serial.available()==0){}; //wait for input
    uint16_t tmp_SN = Serial.parseInt();
    if (tmp_SN==0 || tmp_SN ==0xFFFF){
      Serial.println(F("Invalid SN"));
    } 
    else {
      EEPROM.put(SN_ADDR,tmp_SN);
      EEPROM.get(SN_ADDR,serialNumber);
      Serial.print(F("SN successfully set to: "));
      Serial.println(serialNumber);
    }
  }
}

void getDataLoggerSettings(){
  /* With power switching between measurements, we need to know what kind of setup() this is.
     First, check if the firmware was updated.
     Next, check if the GUI connection forced a reset.
     If neither, we assume this is a power cycle during deployment and use stored settings.
  */
  
  //if firmware was updated, take those settings and time.
  uint32_t storedTime;
  EEPROM.get(UPLOAD_TIME_ADDR, storedTime);
  if (uploadDT.unixtime() != storedTime) {
    newFirmware = true;
    startup.module.clk = RTC.begin(); //reset the RTC
    RTC.adjust(uploadDT);
    
    EEPROM.put(UPLOAD_TIME_ADDR, uploadDT.unixtime());
    EEPROM.put(SLEEP_ADDR, sleepDuration_seconds);
    Serial.println("Firmware updated");
  }
  //otherwise check if the GUI is connected
  //send a startup message and wait a bit for an echo from the gui
  else if (checkGuiConnection()){
    receiveGuiSettings();
  }
  else {
    //if no contact from GUI, read last stored value
    EEPROM.get(SLEEP_ADDR, sleepDuration_seconds);
    startup.module.clk = true; //assume true if logger woke up.
  }
  if(sleepDuration_seconds < 5){
    sleepDuration_seconds = 0;
  }
}


void checkModuleStartup(){
  //intialize & check all the modules
  startup.module.sd = sd.begin(pChipSelect, SPI_SPEED);
  if (!startup.module.sd) serialSend("SDINIT,0");
  
  //Evaluated in getDataLoggerSettings()
  if (!startup.module.clk) serialSend("CLKINIT,0");

  bool turb_temp, pt_temp;
  sensors.begin(turb_temp, pt_temp);
  startup.module.turb = turb_temp;
  startup.module.pt = pt_temp;
  if (!startup.module.turb) serialSend("TURBINIT,0");
  if (!startup.module.pt) serialSend("PTINIT,0");

  //if we had any errors turn off battery power and stop program.
  //set another alarm to try again- intermittent issues shouldnt end entire deploy.
  //RTC errors likely are fatal though. Will it even wake if RTC fails?
  if (!(startup.b == 0b00001111)) {
    Serial.println(F("$Startup failed*66"));

    if (sleepDuration_seconds>5){
      sensorSleep(RTC.now().unixtime(), sleepDuration_seconds);
    } else {
      while(true); //wait forever.
    }
  }
}


void getSensorSettings(){
  //if we have established a connection to the gui,
  //send a ready message and wait for a settings response.
  if (newFirmware || guiConnected){
    sensors.setMeasurementFlags(measFlags);
    sensors.setBackscatterCurrent(iredCurrent/10);
  } else {
    sensors.loadSettings();
  }
}

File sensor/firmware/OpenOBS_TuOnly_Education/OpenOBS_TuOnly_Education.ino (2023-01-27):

/* TODO
 * Troubleshoot the time settings. Dates from RTC are wrong. Firmware date correct.
 * Check sensor initialization with message exchange.
 * Sleep cycling
 *  full shutdown like original?
 *  soft shutdown is likely a lot easier to manage
 * Figure out optimal batching of iridium messages
 *  Maximum time between messages?
 *  Sending less often might save money (e.g. 50 bytes fits 2.5 messages)
 * Battery power
 *  Test solar setup from Adafruit
 *  do we need to bother with full shutdown like autonomous?
 * 
 */

#include <Wire.h>               //standard library
#include <SPI.h>                //standard library
#include <EEPROM.h>             //standard library
#include <SdFat.h>              //Version 2.0.7 https://github.com/greiman/SdFat //uses 908 bytes of memory
#include <DS3231.h>             //Updated Jan 2, 2017 https://github.com/kinasmith/DS3231
#include "Adafruit_VCNL4010.h"


//firmware data
const DateTime uploadDT = DateTime((__DATE__),(__TIME__)); //saves compile time into progmem
const char contactInfo[] PROGMEM = "If found, please contact tlang@live.unc.edu"; 
const char dataColumnLabels[] PROGMEM = "time,ambient_light,scattered_light";
uint16_t serialNumber; 

//connected pins
#define pChipSelect 10              //chip select pin for SD card

//EEPROM addresses
#define SLEEP_ADDRESS 0
#define SN_ADDRESS 500
#define UPLOAD_TIME_ADDRESS 502

//gui communications vars
bool guiConnected = false;
const uint16_t COMMS_WAIT = 500;    //ms delay to try gui connection
const int MAX_CHAR = 60;            //max num character in messages
char messageBuffer[MAX_CHAR];       //buffer for sending and receiving comms

//sensors
Adafruit_VCNL4010 vcnl;

//data storage variables
typedef struct single_record_t {
  uint32_t logTime;
  uint16_t tuBackground;
  uint16_t tuReading; 
}; 
single_record_t data;

//initialization variable
typedef struct module_t {
  bool sd:1;
  bool clk:1;
  bool turb:1;
};
typedef union startup_t {
  module_t module;
  byte b;
};
startup_t startup;

//time settings
long currentTime = 0;
long sleepDuration_seconds = 0;
long delayedStart_seconds = 0;
DateTime nextAlarm;
DS3231 RTC; //create RTC object

uint32_t lastRequestTime = 0;

//SD vars
#define SPI_SPEED SD_SCK_MHZ(50)
char filename[] = "YYYYMMDD.TXT"; 
SdFat sd;
SdFile file;


void setup(){
  Serial.begin(115200);
  Serial.setTimeout(50);
  Wire.begin();
  EEPROM.get(SN_ADDRESS, serialNumber);
 
  /* With power switching between measurements, we need to know what kind of setup() this is.
   *  First, check if the firmware was updated.
   *  Next, check if the GUI connection forced a reset.
   *  If neither, we assume this is a power cycle during deployment and use stored settings.
   */
  //if firmware was updated, take those settings and time.
  uint32_t storedTime;
  EEPROM.get(UPLOAD_TIME_ADDRESS,storedTime);
  if(uploadDT.unixtime()!=storedTime){
    EEPROM.put(UPLOAD_TIME_ADDRESS,uploadDT.unixtime());
    EEPROM.put(SLEEP_ADDRESS,sleepDuration_seconds);
    Serial.println("Firmware updated");
    startup.module.clk = RTC.begin(); //reset the RTC
    RTC.adjust(uploadDT);
  }  
  //otherwise check if the GUI is connected
  //send a startup message and wait a bit for an echo from the gui
  else if (checkGuiConnection());
  else {
    //if no contact from GUI, read last stored value
    EEPROM.get(SLEEP_ADDRESS,sleepDuration_seconds);
    startup.module.clk = true; //assume true if logger woke up.
  }

  //intialize & check all the modules
  startup.module.sd = sd.begin(pChipSelect,SPI_SPEED);
  if(!startup.module.sd) serialSend("SDINIT,0");
  
  if(!startup.module.clk) serialSend("CLKINIT,0");

  startup.module.turb = vcnl.begin();
  vcnl.setLEDcurrent(5);
  vcnl.setFrequency(VCNL4010_250);
  if(!startup.module.turb) serialSend("TURBINIT,0");

  //if we had any errors turn off battery power and stop program.
  //set another alarm to try again- intermittent issues shouldnt end entire deploy.
  //RTC errors likely are fatal though. Will it even wake if RTC fails?
  if(!(startup.b && 0xFF)){
//    nextAlarm = DateTime(RTC.now().unixtime() + sleepDuration_seconds);
//    sensorSleep(nextAlarm);
  }

  //if we have established a connection to the java gui, 
  //send a ready message and wait for a settings response.
  //otherwise, use the settings from EEPROM.
  if(guiConnected){
    receiveGuiSettings();
  }

  if(delayedStart_seconds>0){
    nextAlarm = DateTime(currentTime + delayedStart_seconds);
    sensorSleep(nextAlarm);
  }
  
  updateFilename();
  sprintf(messageBuffer,"FILE,OPEN,%s\0",filename);
  serialSend(messageBuffer);
}


void loop()
{
  //set the next alarm right away. Check it hasn't passed later.
  nextAlarm = DateTime(RTC.now().unixtime() + sleepDuration_seconds);
  RTC.enableAlarm(nextAlarm);
  setBBSQW(); //enable battery-backed alarm

  //Replace data fields with new sensor data.
  data.logTime = RTC.now().unixtime();
  data.tuBackground = vcnl.readAmbient();
  data.tuReading = vcnl.readProximity();
  writeDataToSD(data);
  
  Serial.println();
  Serial.print(data.tuBackground);
  Serial.print(",");
  Serial.println(data.tuReading);

  //ensure a 5 second margin for the next alarm before shutting down.
  //if the alarm we set during this wake has already passed, the OBS will never wake up.
  long timeUntilAlarm = nextAlarm.unixtime()-RTC.now().unixtime();
  if(timeUntilAlarm > 5){
    delay(1000); //give the SD card enough time to close the file and reshuffle data.
    serialSend("POWEROFF,1");
    RTC.clearAlarm(); //turn off battery
    //mimic power off when provided USB power
    delay(sleepDuration_seconds*1000); 
  }
}

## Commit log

2022-09-20 new data packet fields
    Added barometric pressure and air temperature to struct. Rearranged fields to make it simpler to parse.
2022-10-03 added battery monitoring
2022-11-22 Tu only sensor
    1" turbidity sensors for January outreach work in Alaska.
2023-01-27 updated battery voltage reading
2023-02-17 migrated libraries into the sketch folder.
    [BOM_OpenOBS_328p_USB_2023-02-02.csv, PickAndPlace_OpenOBS_328p_USB_2023-02-02.csv]
2023-03-02 Pressure-based autocalibration
2023-03-02 wrong indices on calibration values
2023-03-05 I2C address argument to MS5803 constructor
    Address was hardcoded to 0x76 in the old library. With this modification, we can use two MS5803 sensors- one for water depth and one for barometric correction.
2023-03-08 Fix time check before sleeping
    Previously, a simple limit of sleepDuration > 5 seconds was required to enter sleep. In the event of a prolonged measurement cycle (from slow sensor response or SD card shuffling, the alarm we set at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
2023-03-08 updated PCB Assembly files
    [BOM_OpenOBS_328p_USB_2023-02-02.csv, BOM_PCB_VCNL4010_2023-03-07.csv, PickAndPlace_OpenOBS_328p_USB_2023-02-02.csv, PickAndPlace_PCB_VCNL4010_2023-03-07.csv]
2023-03-10 PCB updated with flat flex option
    [BOM_OpenOBS_328p_USB_2023-02-02.csv, BOM_OpenOBS_328p_USB_2023-03-10.csv, BOM_PCB_VCNL4010_2023-03-10.csv, PickAndPlace_OpenOBS_328p_USB_2023-02-02.csv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]
2023-03-21 included ref for the phototransistor fix.
    Image supporting the new discussion topic on fixing rev1 PCBs.
2023-04-14 rescale pressure for MS5803 mods
2023-04-25 reorganized hardware files.
    [BOM_OpenOBS_328p_USB_2023-03-10.csv, BOM_PCB_VCNL4010_2023-03-10.csv, PickAndPlace_OpenOBS_328p_USB_2023-03-10.csv, PickAndPlace_PCB_VCNL4010_2023-03-10.csv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]
2023-04-26 added parts & materials page.
2023-04-26 material page typo...
2023-05-05 Iridium documentation
    [sensor_head_single.3mf]
2023-06-21 Optional flat flex PCBs
    A short 4-wire flat flex cable makes the sensor head assembly much easier, but requires some custom PCBs. Easier for large quantities.
    [BOM_PCB_VCNL4010_2023-03-10.csv, BOM_PCB_VCNL4010_2023-06-08.csv, PickAndPlace_PCB_VCNL4010_2023-03-10.csv, PickAndPlace_PCB_VCNL4010_2023-06-08.csv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]
2023-07-21 Overhaul docs to match new sensor head.
    [clampingCaul_v2_5x.3mf]
2023-08-02 now supports all 3 epoxy pours
    [clampingCaul_v2.3mf, clampingCaul_v2_5x.3mf]
2023-08-02 Added EasyEDA schematic and board files.
2023-08-02 replaced out of stock parts
    [BOM_OpenOBS-328_2023-08-02.csv, BOM_OpenOBS_328p_USB_2023-03-10.csv, PickAndPlace_OpenOBS-328_2023-08-02.csv, PickAndPlace_OpenOBS_328p_USB_2023-03-10.csv]
2024-07-05 Alternate PCBA files for microsd shortage
    [BOM_OpenOBS_328p_replacementSD_2024-07-05.csv, PickAndPlace_OpenOBS_328p_USB_2024-07-05.csv]
2024-07-05 single board gerbers
    [BOM_OpenOBS_328p_replacementSD_2024-07-05.csv, PickAndPlace_OpenOBS_328p_USB_2024-07-05.csv]
2024-09-06 Added single VCNL4010 board files.
    [BOM_VCNL4010_single_2024-09-06.csv, PickAndPlace_PCB_VCNL4010-2024-09-06.csv]
2025-02-07 Added pressure filter for off-the-shelf pcbs
    [pressure_filter.stl]
2025-03-27 Major cleanup
    Moved sensor config and reading to separate file.
2025-03-27 Added sensor disable in software.
2025-03-28 Updated sensor head with removable filter
    [PressureFilter_V3.stl, SensorHead_V3.stl, sensorHead_v2_noPressure.3mf, sensor_head_m3bolt.stl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]
2026-02-25 added design files for sensor head and caul
    [OpenOBS_clampingCaul v10.f3z, OpenOBS_clampingCaul v10.step, sensorhead_v2_filterBolt v3.step, sensorhead_v2_filterBolt v4.f3d]
